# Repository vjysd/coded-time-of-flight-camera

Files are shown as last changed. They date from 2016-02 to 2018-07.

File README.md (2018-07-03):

# Coded Time of Flight Imaging System

## Motivation
Depth accuracy has always been an issue with range imaging technologies. Conventional continuous wave time of flight imaging technologies face multipath, scattering and reflection artifacts. Ultrafast imaging got fascinating ever since Doc Edgerton synchronized his electronic stroboscope with a special high-speed motion-picture-camera so that with each flash, exactly one frame of film was exposed. Visualizing and capturing action at speeds beyond human perception will help us in studying a lot of physical phenomenon like scattering, reflection, and interaction with matter. Here we propose a coded time of flight imaging technique to capture light in motion and to ameliorate depth accuuracy.

## Idea
To address the above mentioned issues, we constructed a coded time of flight camera using the PMD 19k-S3 sensor. This involved design of cyclone IV FPGA, soft core processor programming & optical system development. We carefully chose a broadband code instead of a continuous wave to modulate image sensor and light source. A detailed instrumental manual to build your own coded time of flight camera can be found at the end of this page.

## Approach
We exploited the concept of time resolved imaging to capture light in motion. A phase modulated light source locked with image sensor served this purpose. To address the issue of depth accuracy as our second intent, we constructed a mathematical model of multi-frequency light source de-multiplexing, wherein multiple light sources running at different frequencies were used to improve depth accuracy. A broadband signal, accommodating all the bins from multiple light sources was used to modulate the image sensor. This method proved to be more economical and efficient than current models where multiple cameras are used to serve the same purpose.

## HOW TO
Please use the diy_tof.pdf file to find all the necessary information about rebuilding the system from scratch.

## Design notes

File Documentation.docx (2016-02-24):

ToF Ultra-fast Imaging Camera (Documentation)

Basic Block Diagram:

(This part of the document portrays the important block diagrams which model the system operation.)

Code Database:

(This part of the document depicts various modules/functions/codes which control the overall data and control flow within the scope of the project.)

Verilog modules:

Verilog modules establish an interface between PMD Sensor, ADC and FPGA board and controls their whole operation.

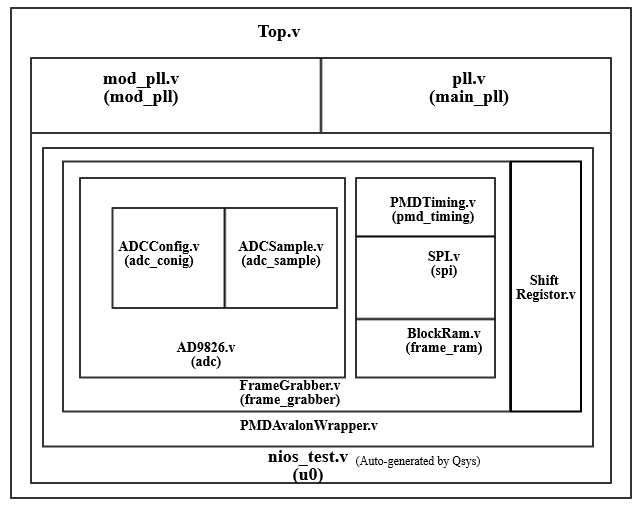
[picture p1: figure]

(Fig2: Verilog Module Flow)

- ADCConfig.v

This FSM configure the FPGA and ADC for a bi-directional data flow. It has three states,

A. STATE_ADDRESS -- Sends the R/W bit, and the three address bits
B. STATE_DELAY -- Pause the operation for few cycles
C. STATE_DATA -- Sends out the 9-bit data word
- ADCSample.v

This FSM controls the Sampling of ADC and the Readout process. It has three states

A. STATE_IDLE -- Waits for the sample_en signal to go high
B. STATE_SAMPLE -- Sample and Hold
C. STATE_READOUT -- Pushes the data into the Bus
- AD9826.v

Instantiates the ADCConfig.v & ADCSample.v and controls the whole ADC bi-directional flow with FPGA.

- PMDTiming.v & SPI.v

These module controls the whole timing operations of the PMD Sensor. They have 16 different states to control the whole flow of IDLE, RESET, INTEGRATION, READOUT, COOLDOWN for PMDTiming, & STATE_DATA, STATE_IDLE, STATE_ADDRESS for SPI . Each of these states meet the timing requirements specified by the PMD Datasheet.

http://web.media.mit.edu/~achoo/pr/19k3_datasheet.pdf

- BlockRam.v

This module controls the reading and writing of ADC readout in and out of FPGA temporary

memory. The data from ADC is moved into a temporary register and then pushed into the Ethernet for data visualization on PC.

- FrameGrabber.v

FrameGrabber instantiates PMD_timing, SPI, BlockRam & AD9826. This FSM has various states to control,

1. Setting frame size.
2. Grabbing the captured frame from the FPGA temporary memory.
- ShiftRegister.v

ShiftRegister module helps in driving the modulating signal to the light source and to the MODSEL terminal of the PMD Sensor.

- PMDAvalonWrapper.v

FrameGrabber is instantiated in this module. It interacts with the C-codes via the address bus and helps to set the Integration time & modulation mode. Since the C-code and the PMDAvalonWrapper are in unison through the address bus, the above specified values can also be set during the compilation of C-codes.

All the above specified modules are fed into the Qsys Library, and when the Qsys is generated, it automatically compiles all the Verilog codes and provides a single interfacing code named nios_test.v.

Qsys can be accessed by going into Tools→ Qsys

- PLL.v

This is a module that is auto generated by using the Megawizard plug-in manager Wizard.

This can be accessed by going into Tools → Megawizard plug-in manager. The interactive GUI guides through the process of configuring the PLL for user requirements.

Here we use PLL.v to generate clock signals of different frequencies, but same phase(i.e. 0). These clocks are used to drive various blocks in the FPGA.

- mod_pll.v

This is a module that is auto generated by using the Megawizard plug-in manager Wizard. Here we use mod_pll, to generate two output clocks of same frequency, but one clock signal configured for dynamic phase reconfiguration. The latter one is fed into the light source, and the former into the MODSEL signal of PMD sensor.

- top.v

This is highest in the hierarchy, and instantiates three modules, i.e. PLL, mod_pll & the nios_test. This acts as a wrapper for the whole Verilog code base.

MATLAB Code & functions:

Matlab codes and functions helps in reading the data from the FPGA ethernet adapter into the Computer and Visualization of the read data.

- pmd_connect.m

This function establishes a tcp/ip connection with the FPGA at a specified port and ip address.

- pmd_read_image.m

This function reads the image data via the tcp port, and shapes it to a specified frame rate and stores it in a variable named rawCorr.

- pmd_phase_step.m

This function writes through the ethernet, specifying the FPGA to increase/decrease the phase of the Light Source.

- pmd_600.m

This matlab code calls the pmd_read_image and thereby captures the frames. The number of frames to be captured can be set in this code. After the frame capture is done, code automatically gets takes the FFT of the frames, and stores it in a variable named rawCorrFFT, and then it plots the angle and the amplitude images using the mview.m function.

- mview.m

This matlab function, inputs the frames captured and provides an interactive GUI to move through all the frames using a mouse scrollbar, and also provides an option to play it at specified frame rates.

C-codes:

C-codes builds a framework to establish a TCP connection between the FPGA board and Computer. These codes program to the soft core processor onboard DE2-115 & help in memory allocation. Alongside that, these codes also helps user to set the Integration time without disturbing the Verilog codebase.

There are mainly two project database to handle the C codes.

- pmd_tcp_bsp

This project helps to generate the Board support packages (BSP) & helps to re allocate the memory changes made in the Verilog code. In order to change update the BSP,

Goto Project Explorer → Right click on pmd_tcp_bsp → Nios 2 → Generate BSP.

- pmd_tcp

This is the C project which controls the whole interface operation. hello_ucosii.c is the main code that is can be used to update the integration time. This code, dumps the Memory write and retrieval code into the soft core processor and establish a bidirectional communication between FPGA and Computer.

FPGA Documentation:

This part of the guide helps in setting up the FPGA board (i.e Altera DE2-115 in this case), to control the timing requirements of PMD 19K-S3 and other peripherals.

There are two ways of setting up the whole environment,

1. Experience the taste of Verilog by setting up everything from Scratch! (We give the codes though).

2. Use the archived project to directly set up the environment.

Setting up required softwares:

1. Quartus ii web edition:

https://www.altera.com/download/software/quartus-ii-we/12.0sp2

2. Nios ii tools:

Download both Version 12.0 and Service pack 2.

https://www.altera.com/download/software/nios-ii/12.0

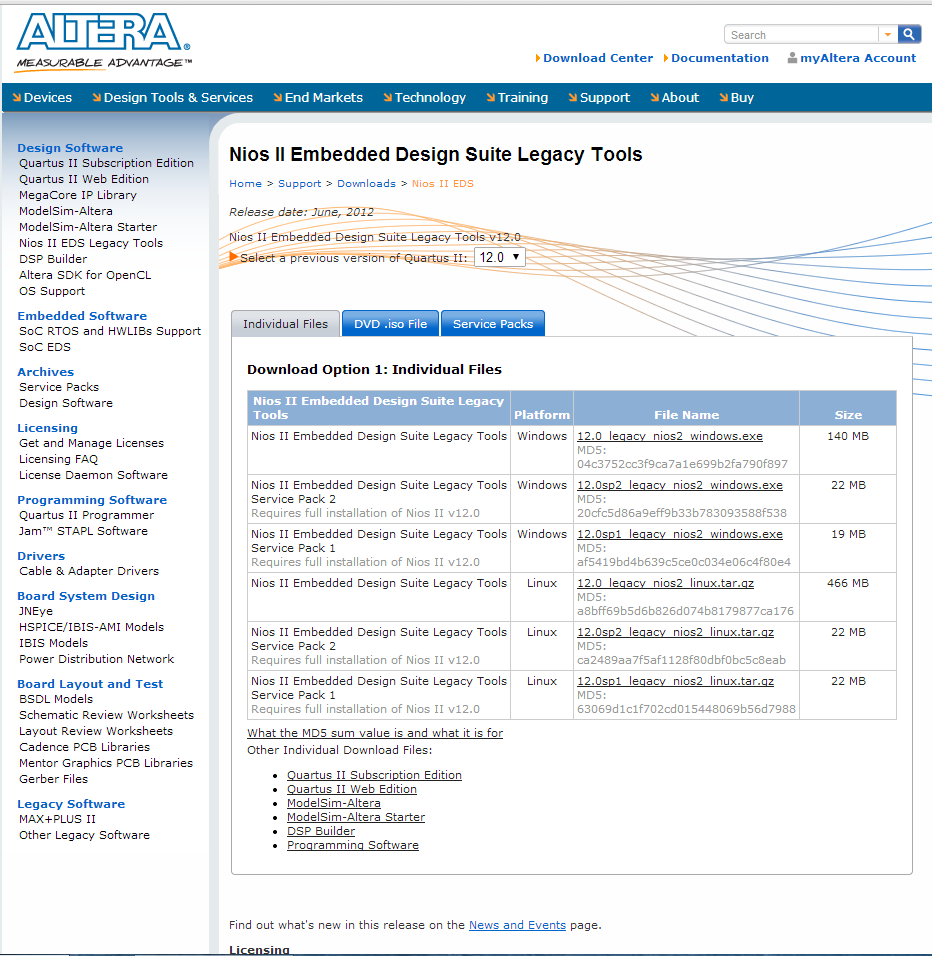
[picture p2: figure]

3. Matlab (Version 2012 or above is preferred).

Steps:

Here are the steps to set up the whole Verilog environment from scratch

1. Once all the softwares are installed and setup, open up Quartus ii → New Project Wizard.

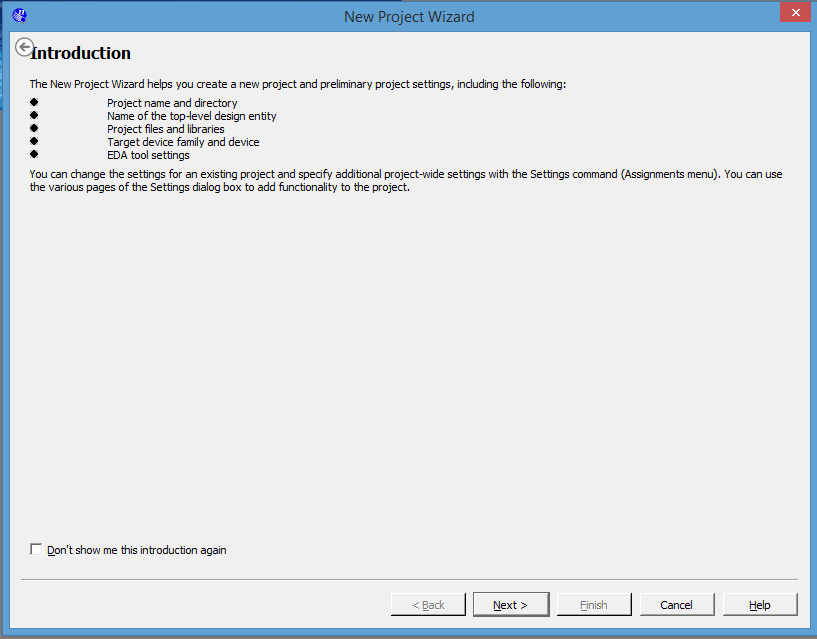
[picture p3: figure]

2. Click on Next, and the window below will pop- up.

- Set the default directory of the project.
- Give a name to the project! (We call this a Nano-Cam!).
- You may define the top level entity as “top”, but we can always modify this later.

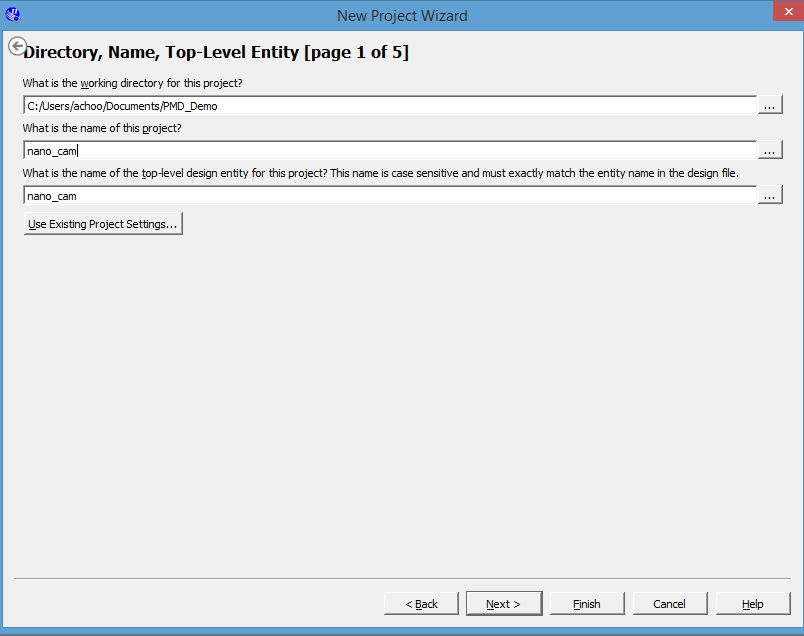
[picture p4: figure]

3. We will be adding all the design files later on, so you can just click on next on the below window.

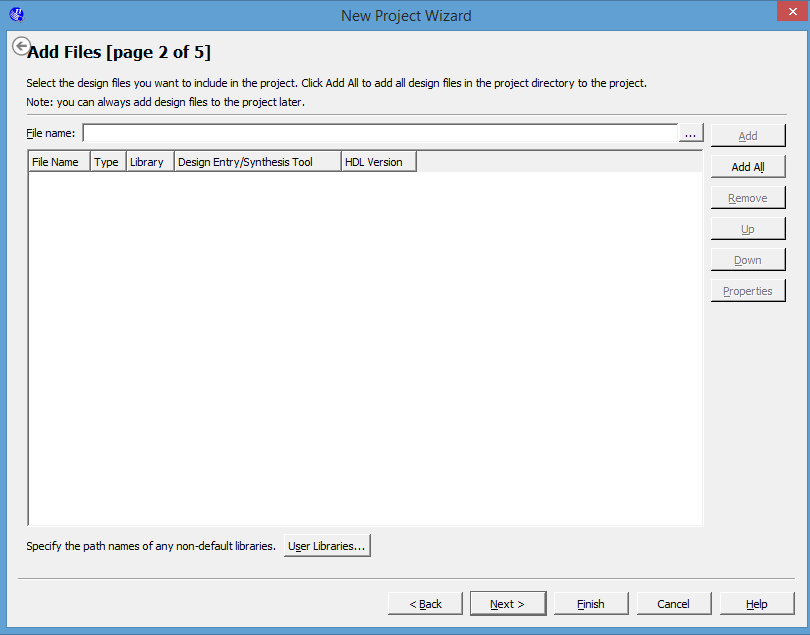
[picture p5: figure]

4. This page defines the FPGA Family and the device we are using.

- Select the Family to be Cyclone 4 E.
- And the device will be EP4CE115F29C7
- Click on next to move forward.

5. This window is to add EDA tools for additional simulation and Verifications, which we can skip and move into next window.

- Finish the project setup wizard.

6. Now we will setup the System map. To do this,

Click on Tools → Qsys, on the top left tab.

7. Once Qsys is up and running, we should see a window below.

8. Now we need to add all the libraries we need,

- On the left, click on Embedded Processors → Nios ii Processor.

Select the core to be Nios ii/s and then click on finish.

- Click on Memories and Memory Controllers → External memory interfaces → SDRAM Interfaces → SDRAM Controller.

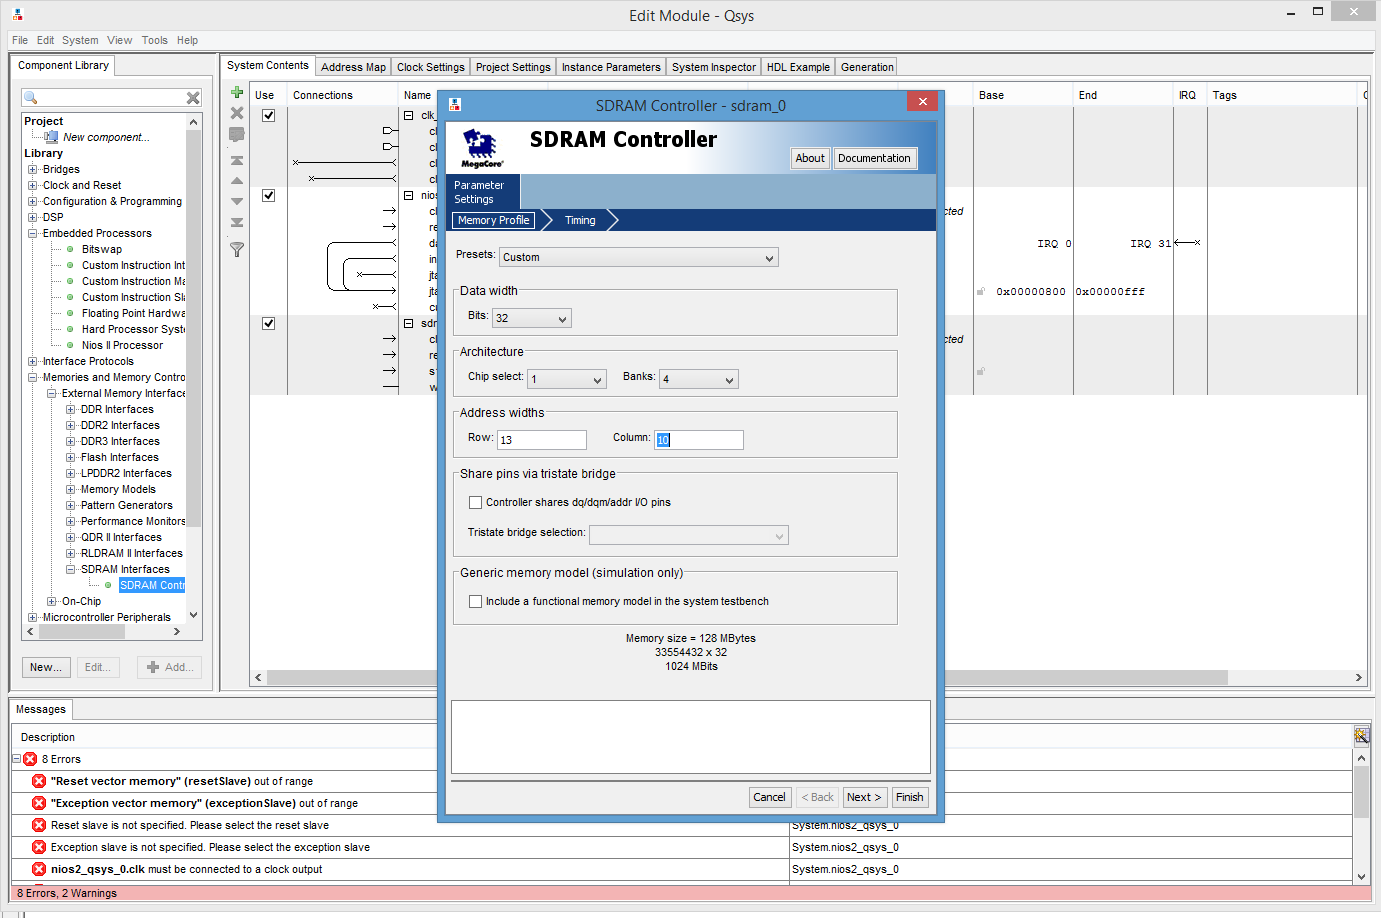
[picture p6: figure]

Select and set the values/parameters as indicated by the figure, and click next.

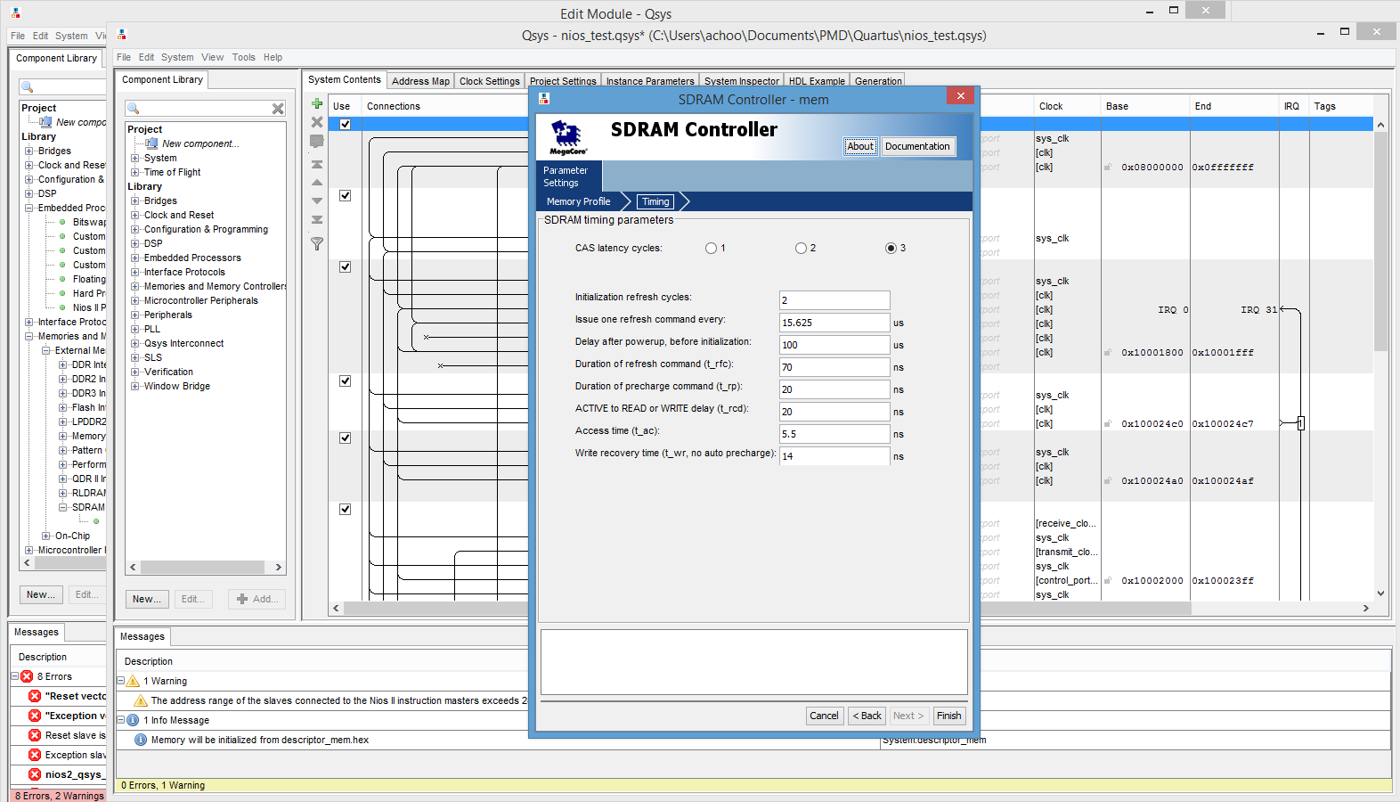
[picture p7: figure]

Now leave the timing parameters as it is and click on Finish.

- Click on Interface Protocols → Serial → JTAG UART to create a new JTAG library from your left pane.

Once the window appears, do not change any settings, click on finish.

- Click on Interface Protocols → Ethernet → Triple Speed Ethernet.

Now follow the below images clicking next, to complete the ethernet library setup. Please enter the values specified in the images to their respective fields.

- Click on Bridges → DMA → Scatter-Gather DMA.

Once the window opens up,

Choose Transfer Mode : Stream to Memory and click on finish.

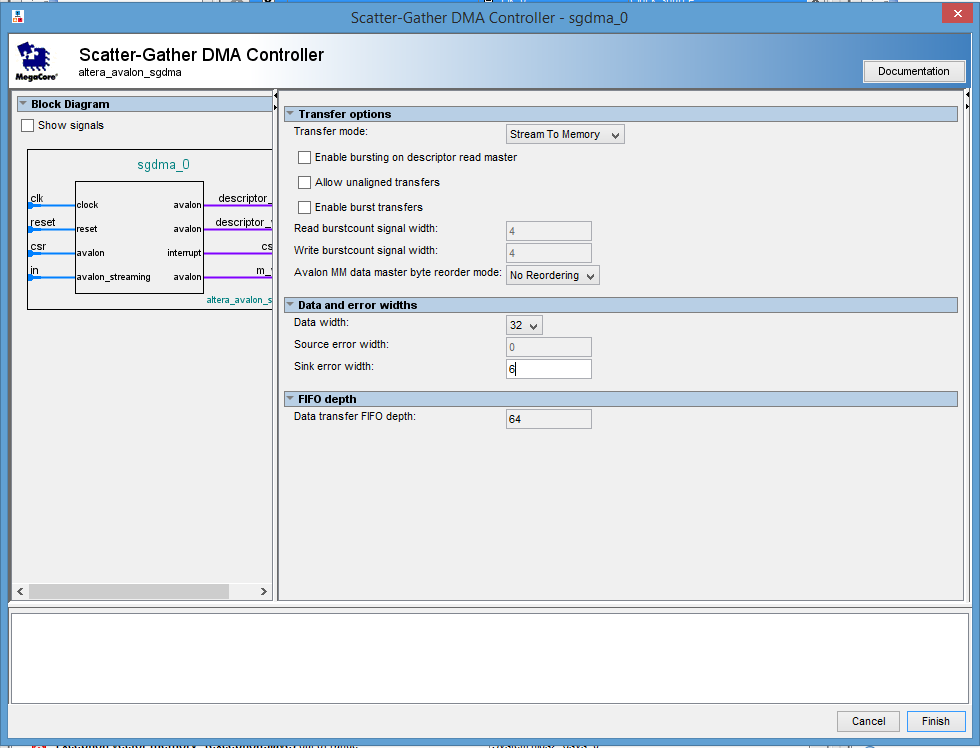
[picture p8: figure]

Repeat the above steps to create another Scatter Gather DMA,

Choose Transfer mode here as: Memory to Stream and click on finish.

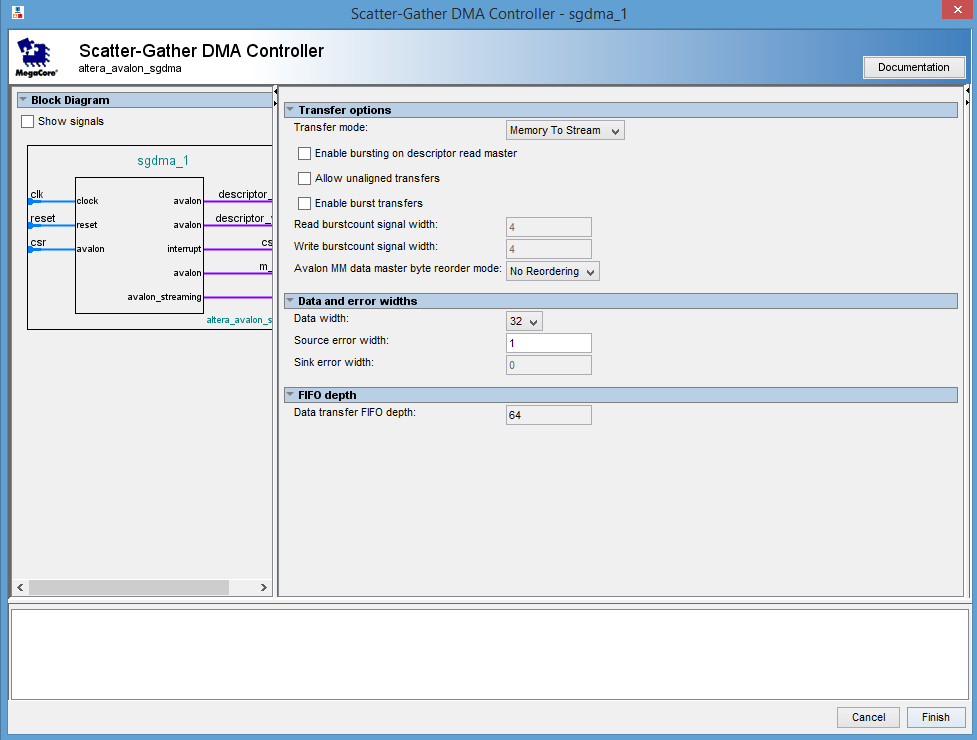
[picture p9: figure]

- Click on Memories and Memory Controllers → On Chip → On Chip Memory (RAM).

Once the window open up, do not edit anything, just click on finish.

- Click on Peripherals → Microcontroller Peripherals → Interval Timer.

Once the window appears click on finish without editing anything.

- Now, we will add our custom library for the Sensor, click on File → New component.

Now enter the following information into the text fields to create the library, and click next.

Click on the “+” button at the left corner to add the verilog files.

After clicking the button, navigate to the folder which is named “Verilog”, within the supplied codebase.

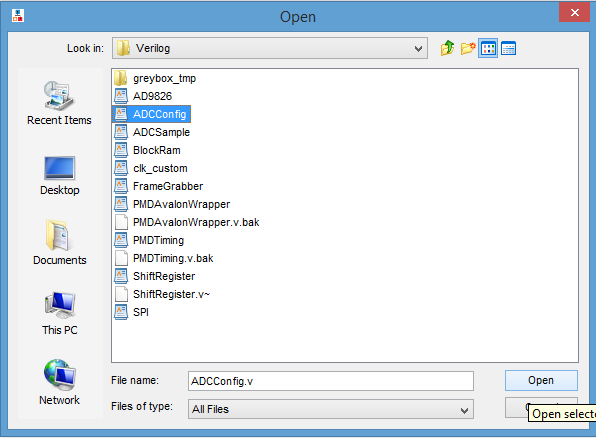
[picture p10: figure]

Select a file and click open. Repeat the above steps till you add all the files in Verilog directory.

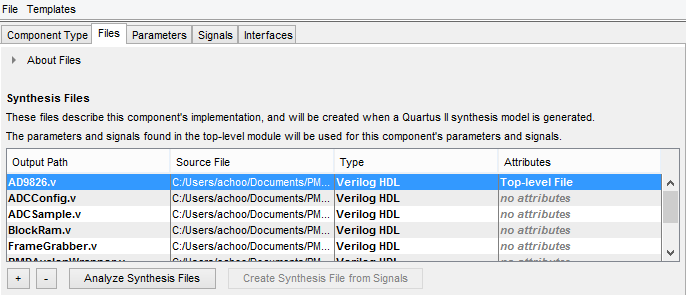
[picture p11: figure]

After all the files are added, the wizard automatically assigns Top-level attribute to the file on the top of the list!! But our top level module is PMDAvalonWrapper. So click on the attribute field on ADC9826, and uncheck top-level attribute.

Navigate to the PMDAvalonWrapper, and set the attribute to be top level file.

Click on ok, and then click on Analyse Synthesis Files. Once the analysis is done, close the console which pops up.

Now click on the Signals tab from the above pane, to edit the signal attributes.

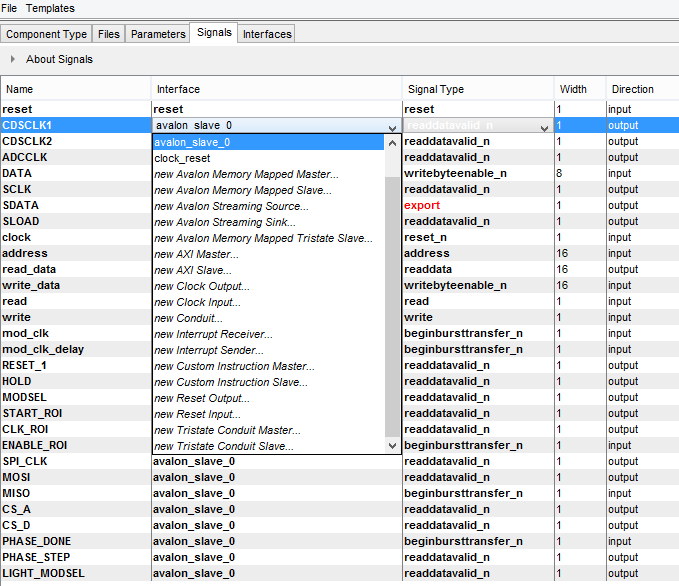
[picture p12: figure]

Here edit all the signals and assign them the properties as shown in the below figure,

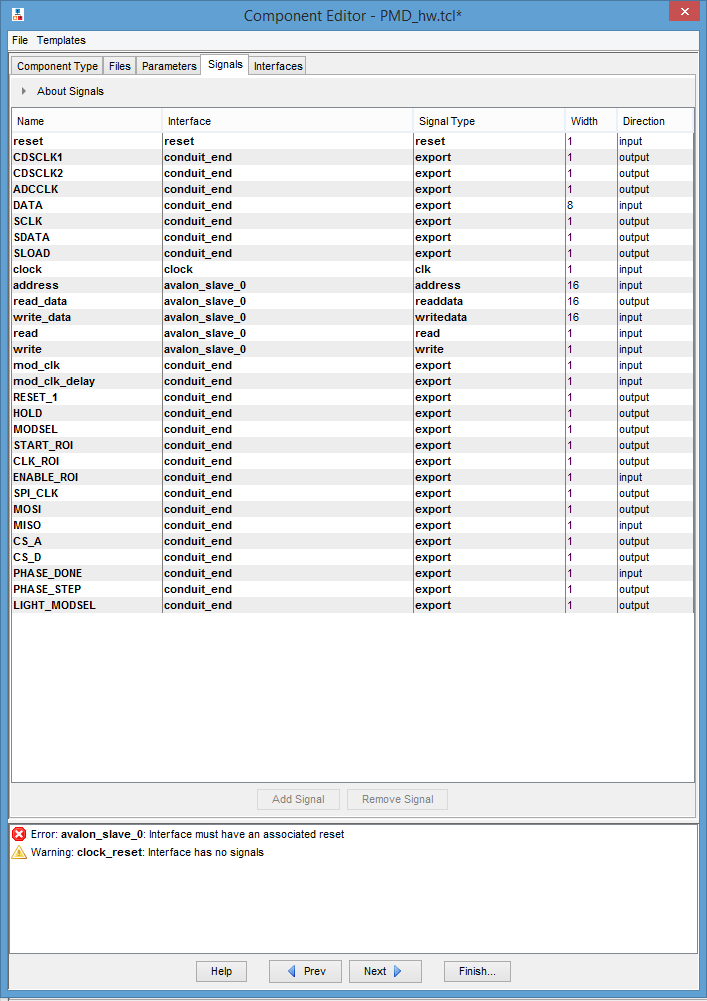
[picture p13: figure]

Once all the signals are edited and set to the specified parameters, click on the next button.

Now go to the interfaces tab, where in select the “clock_reset(Reset input)” interface and click on Remove interfaces with no signal.

Click on finish to add the Custom Library to our system.

9. Once we have added all the libraries into the system, now we need to,

- connect the data and address busses for communication. To do this, we need to move the cursor towards the connections part of the Qsys window.
- Also rename all the components as they are present in the images in order.
- Set the export status of few signals and name them accordingly from the Export section as seen in images.

And click on the dots to form the connectivity as shown in the figures.

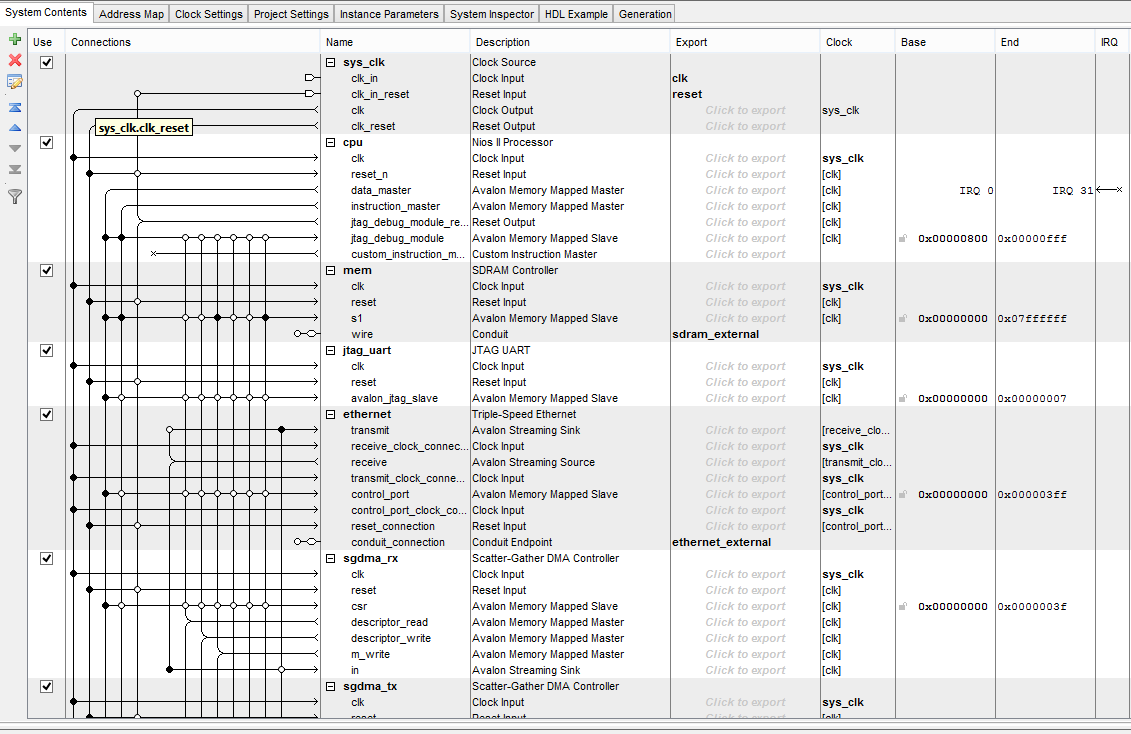
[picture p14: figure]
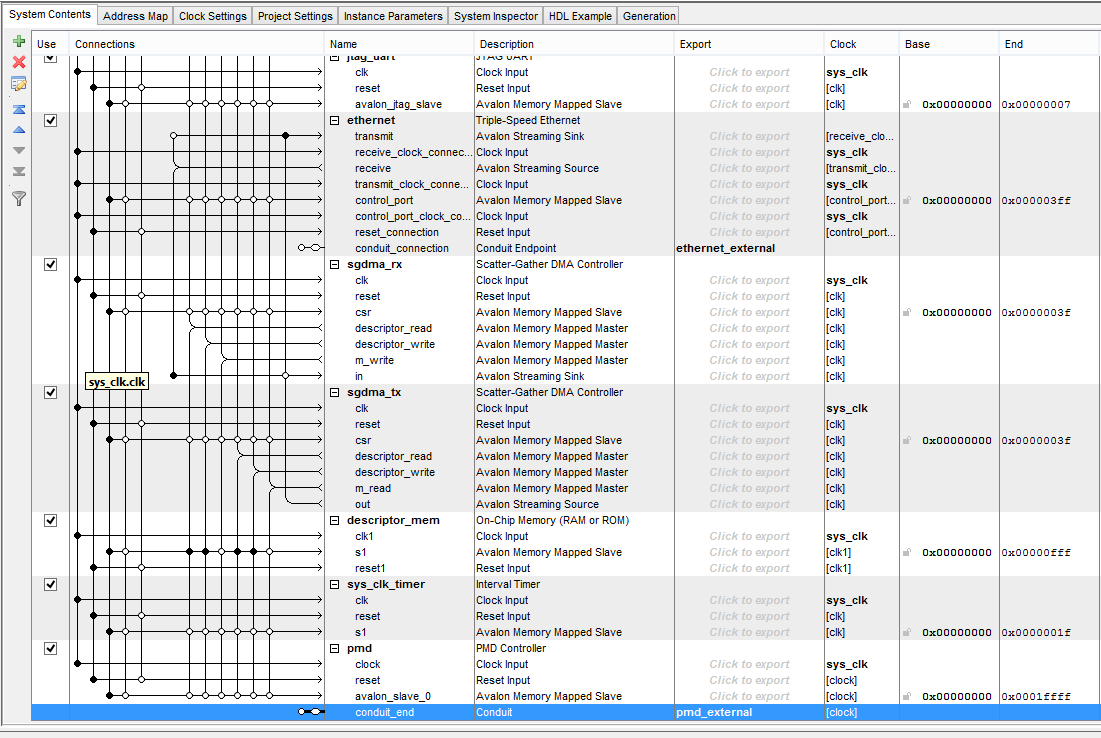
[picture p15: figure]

Once the renaming, connectivity & export assignment is done,

Click on the System → Assign Base Address.

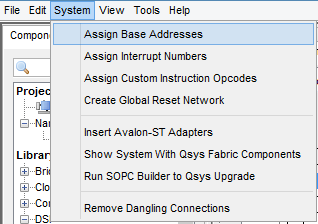
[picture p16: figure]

Now we need to assign the interrupt rank/status to few signals. To do this we will go to the IRQ section in the same Qsys window, and assign values (1, 0, 2, 3) in the tiny boxes there.

Once the interrupt is setup, save the system by going to File → Save or by using (ctrl + S).

Now go into the Generation tab in Qsys, and click on Generate to create the System!

10. Once generate is complete, close the Qsys window. And go back to the Quartus ii project we had created.

11. Click on the Project → Add files into the project.

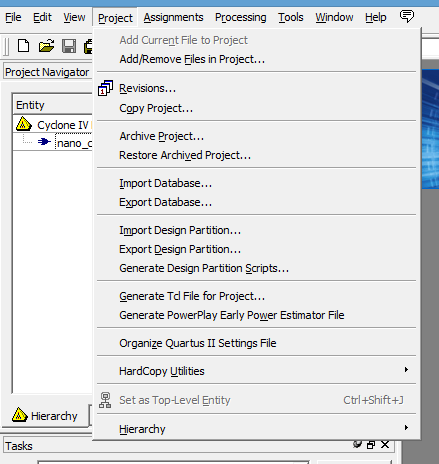
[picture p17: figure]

12. Add the nano_cam.qsys file we just created from the previous steps. To do so, browse to the project location (Done by default).

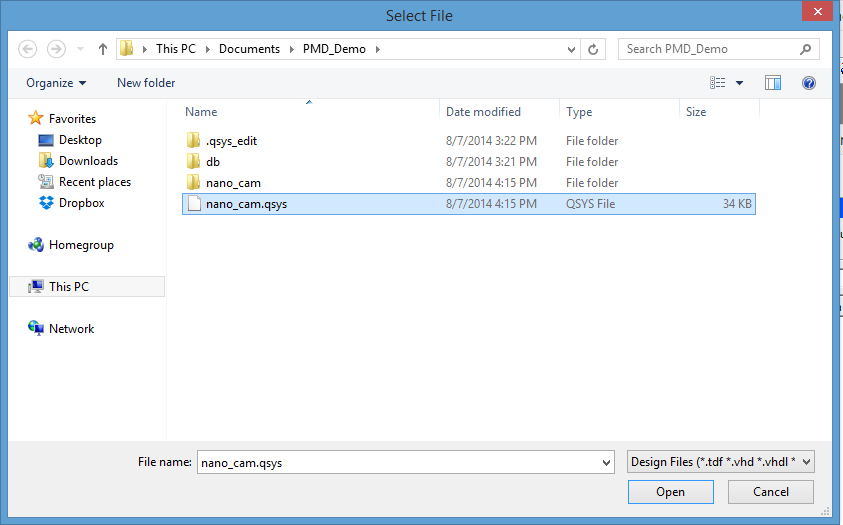
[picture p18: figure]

13. Add top.v file which is provided in the code database by the same steps.

14. We now have to create two PLL (Phase locked loops) to control the light and Sensor modulation. To do this, click on Tools → Megawizard Plug In manager → Create a new custom megafunction variable.

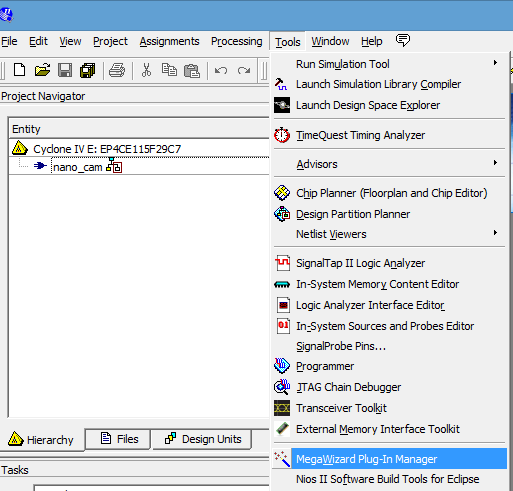
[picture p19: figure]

Search for ALTPLL,

Specify the name of the output file as “pll” and click next.

Follow the below images to navigate through each window and set the parameters likewise. Keep clicking on next to go into next window.

Click on finish to complete the creation of the PLL. If a window pops up asking to automatically update the IP, click OK.

Now similarly we have to create another PLL, named “mod_pll”. This is to give a dynamic phase to one of the signal fed to the light source.

To do this, follow the steps depicted in the pictures below.

(Note that here only two output clocks are used, i.e c0 & c1).

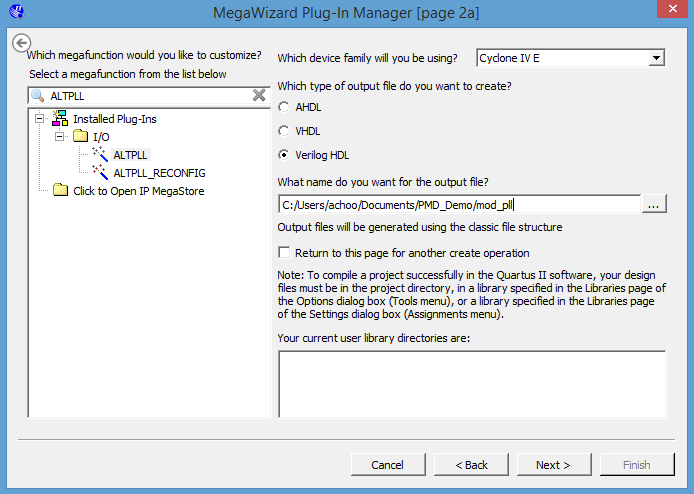
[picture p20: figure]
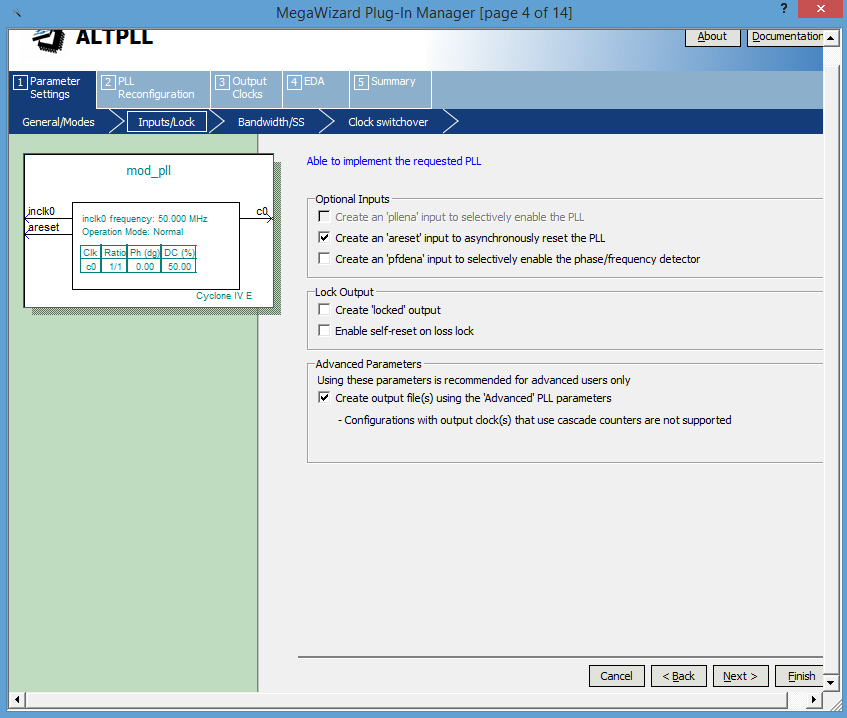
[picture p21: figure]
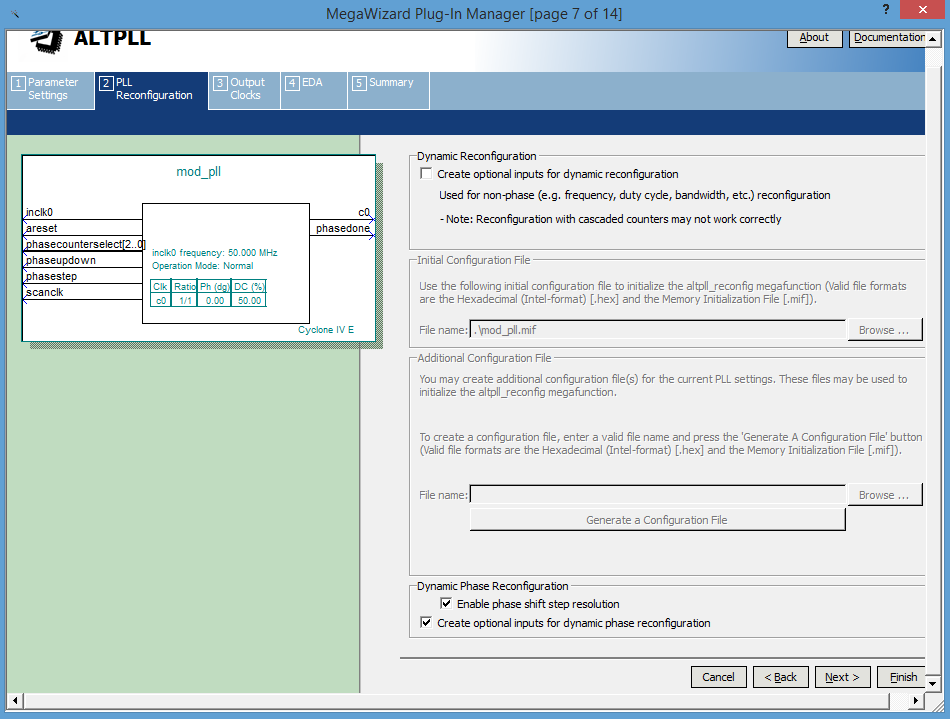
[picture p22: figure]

Here we enable the Dynamic Phase reconfiguration and then the Enable phase step resolution.

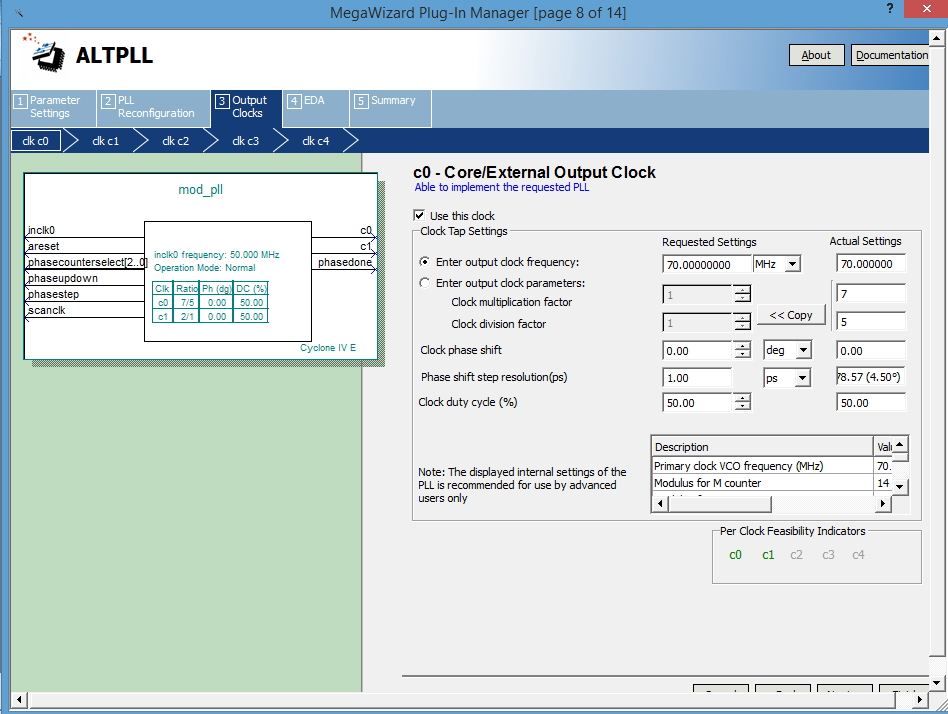
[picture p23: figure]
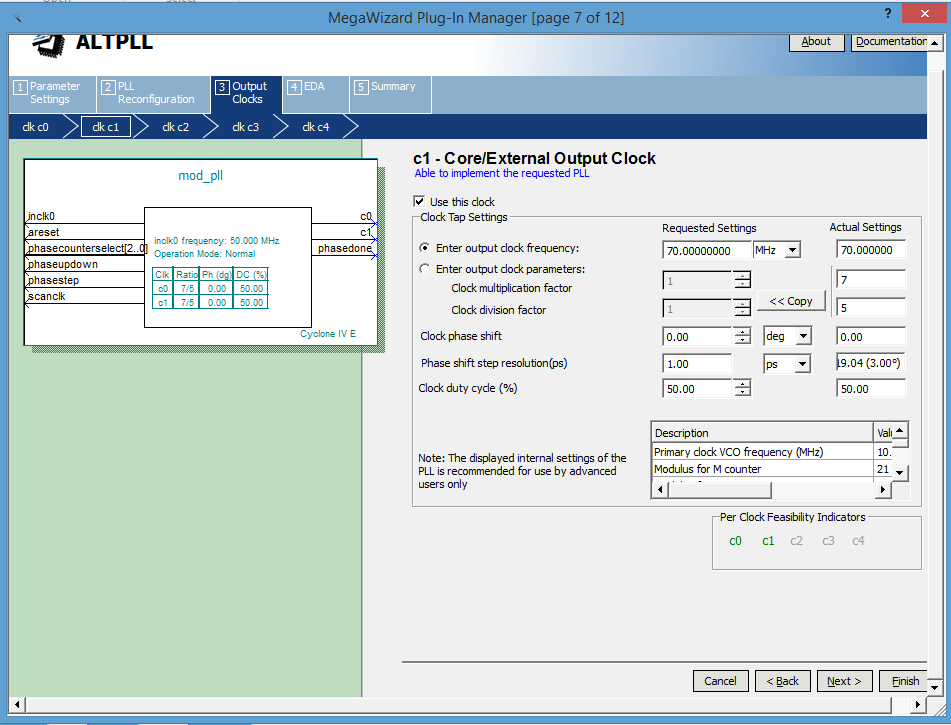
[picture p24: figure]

Click on finish to complete the create the PLL.

15. Now we need to add an IO extension as well for clocking an external pin. To do this, go to Tools → Megawizard Plug In Manager → Create new custom megafunction variation.

Now search for IO, and select “ALTDDIO_OUT”.

Click on next and follow the images below to complete the whole setup.

16. Click on the files tab in the project navigator. And set the top.v as the top level Entity.

17. Finally go to the Assignments → Import Assignments.

Browse to the nano_cam.qsf file which is provided in the code database and click open.

Once this si done, we are ready to compile and program!

18. Click on the Processing → Start Compilation.

This takes around 5-6 minutes to compile and after the we are good to upload and capture some cool depth images!!

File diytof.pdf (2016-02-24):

Vijay Sadashivaiah | Diony Rosa | Achuta Kadambi

### Camera Culture, MIT Media Lab

# Time of Flight – Ultra Fast Imaging Camera

Version
1

# User Reference Manual

# Table of Contents:

### 1. System Architecture

1.1. Block representation
1.2. Brief Overview – Block wise
1.3. Code database & Structure – Language wise

### 2. Printed Circuit Board (Sensor & Light Source)

2.1. Overview on PCB design files
2.2. Circuit Diagrams & Schematics
2.3. Eagle file Database
2.4. Ordering from Sunstone
2.5. Interfacing the PCB’s to FPGA

### 3. Setting up Quartus ii Verilog programming Environment

3.1. Quartus Download & Setup
3.2. Archived project – Importing and Setup
3.3. Compilation and Verification

### 4. Setting up Nios ii hardware interface tool

4.1. Archived project – Importing and Setup
4.2. Compilation and Verification

### 5. Setting up MATLAB programming Environment

5.1. Code Database – Scripts & Functions
5.2. Setting the parameters
5.3. Workflow & Representation

### 6. Calibration and Capture 7. Appendix 1-2

# System Architecture

This part of the document explains the whole system architecture and signal flow within the Camera.

1.1. Block Diagram Representation


(Fig1: Block diagram of various sub elements)

Part
1

1.2. Brief Overview – Block Wise

As seen in the Block diagram, the whole system comprises of 3 main blocks. In this section we will briefly describe each one of them and provide additional resources.

1.2.1. Altera DE2-115 Development kit:

The Altera® DE2-115 Development and Education board was designed by professors, for professors. It is an ideal vehicle for learning about digital logic, computer organization, and FPGAs. Featuring an Altera Cyclone® IV 4CE115 FPGA, the DE2-115 board is designed for university and college laboratory use. It is suitable for a wide range of exercises in courses on digital logic and computer organization, from simple tasks that illustrate fundamental concepts to advanced designs.

Official link to website and purchase information for Academic research: http://www.altera.com/education/univ/materials/boards/de2-115/unv-de2-115-board.html (http://www.altera.com/education/univ/materials/boards/de2-115/unv-de2-115-board.html)

1.2.2. PMD 19K – S3:
The PMD PhotonICs® 19k-S3 is the first commercially available Time-of-Flight 3D chip. The optical sensor enables the real-time capture of distance and gray scale information. Due to the outstanding sensitivity and improved performance of the new PMD Photo-nICs® 19k-S3, high accuracy with extremely low power consumption is achievable. Read-out clocks of 15MPixel/s are possible. Thanks to the integrated SBI (Suppression of Background Illumination) technology, a well-known PMD feature, this innovative product can be deployed in indoor and outdoor environments.

Official link to website:
http://www.pmdtec.com/products_services/pmd_photonics.php


1.2.3. Illumination System:

Illumination forms a very important part of time of flight imaging, and we are using a Laser source to drive our Camera system. We have used a single, LPC-826 Laser diode from Mitsubishi. These are High speed lasers which serves our purpose of bright illumination.

It is very important to choose an efficient driver to handle high current requirements of Laser diode. We used the iC- HG HG1D evaluation board from iC – Haus to efficiently drive the Laser.

1.2.4. Other peripherals and blocks:
- Other than these three blocks, AD9826K is an Analog to Digital converter used to achieve sampling and readout from the Sensor into the FPGA. Timings and operation is again controlled by the DE-115 board.
- Onboard PLL (DE2-115), is used for achieving phase and frequency modulations, thereby providing a phase lock system for the operation of Camera.

- A computer system forms a medium to configure all the peripherals and also to visualize the data captured from the camera. We use mainly three software packages for working with our camera.
a. Quartus ii FPGA programming interface
b. Nios ii Hardware tool package
c. MATLAB
1.3. Code Database:

This part of the document depicts various modules/functions/codes which control the overall data and control flow within the scope of the project.

1.3.1. Verilog modules:

Verilog modules establish an interface between PMD Sensor, ADC and FPGA board and controls their whole operation.


(Fig2: Verilog Module Flow)

Verilog Files/Archive project can be downloaded: http://tinyurl.com/l7gzmnv

1.3.2. Matlab scripts/Functions:

Matlab codes and functions helps in reading the data from the FPGA ethernet adapter into the Computer and Visualization of the read data.

Matlab Files/Scripts can be downloaded at: http://tinyurl.com/oluath7

1.3.3. C-codes Nios interface:

C-codes builds a framework to establish a TCP connection between the FPGA board and Computer. These codes program to the soft core processor onboard DE2-115 & help in memory allocation. Alongside that, these codes also helps user to set the Integration time without disturbing the Verilog codebase.

C-codes can be downloaded at: http://tinyurl.com/l8l4p3o

Here is a link to brief explanation of each module/ function:

http://tinyurl.com/nt3omx5

http://tinyurl.com/jlspyvo (http://tinyurl.com/l7gzmnv)

http://tinyurl.com/jguunla (http://tinyurl.com/nt3omx5)

All the project codes are available here: Download as zip and unzip the files,

https://github.com/vjs347/coded-time-of-flight-camera

# Printed Circuit Board

(Sensor & Light Source)

This part of the Document illustrates the PCB layouts & Circuit diagrams of the light source and Sensor used for the Camera. This forms the first step towards building your own time of flight imaging device.

2.1. Overview:

Circuit Diagrams/Schematics & PCB Design forms the first step towards building any electronic gadget. In our Camera, we have two important PCB designs,

2.1.1. Sensor board Design:

The PMD 19K-S3 sensor from PMD Photonics, is a 40 pin IC. The terminals are interfaced with the ADC and the FPGA to control the timing and readout. It requires precision design capabilities and ideas in designing the whole sensor board. We have used AD9826K ADC for the readout.

2.1.2. Light Source design:
We have used a single, LPC-826 Laser diode from Mitsubishi. These are High speed lasers which serves our purpose of bright illumination. iC- Haus HG1D evaluation board is used to drive these High power Lasers.

Part
2

2.2. Circuit Diagrams and Schematics:

In this section we briefly describe the Circuits/ Schematics used in our design. Appropriate images are added for reference.

2.2.1. Sensor Schematic:
a. Voltage Regulator:


This forms the Voltage regulator circuit to drive/power the PMD Sensor board from the FPGA.

b. 40 Pin connector:


This forms the 40 pin Connector which is the main interface bus between DE2-115 and Sensor board.

c. ADC Circuit:


ADC here works in Sample and hold mode and helps in sampling the analog readout from the sensor and pushes the data into the FPGA through the 40 pin connector.

In the figure the terminals VIDEO01, VIDEO02, VIDEO03 are the input signals
into the ADC and the terminals named ADC00…….ADC07 frames the output of
the ADC data.

d. PMD 19K-S3 Sensor:

All the Signals to control the timing of PMD are coming from the FPGA board.

The whole Schematic image could be found at: http://tinyurl.com/m5ko9k6
https://github.com/vjs347/coded-time-of-flight-camera/tree/master/_PCB/Sensor

2.2.2. Light Source Schematic:

The Schematic and the mapping for HG1D evaluation board can be found here.

http://www.ichaus.de/upload/pdf/HG_datasheet_B2en.pdf

2.3. Eagle File Database:

All the schematics and board design files (both schematic and board) can be downloaded at:

http://tinyurl.com/nj8xxj5

2.4. Ordering from Sunstone:

Sunstone Circuits is one of the most experienced PCB manufacturers in the USA. All the orders can be placed online by uploading the Schematics and the board files.

Official link: www.sunstone.com

2.5. Interfacing the PCB and FPGA:

This section illustrates the steps to be followed to wire up the Sensor board & Light source to the FPGA.

Steps to be followed:

1. Once the PCB’s are fabricated, and soldered with all the components as
in the schematic, the Sensor should look something like this.

https://github.com/vjs347/coded-time-of-flight-camera/tree/master/_PCB/Light_Source/New (http://tinyurl.com/nj8xxj5)


2. Now attach the 40 pin connector to the port in the image and connect the other end to the 40 pin connector on FPGA Development kit. After the connection is done, the system should look like,


3. Once this is done, now we need to hook up the light source, to do this, connect the terminals circled in red on Light source board, to the pins on DE2-115 marked red in the adjacent diagram.


Power up the Evaluation board with plugging VDD and VLDA to ~4V. This completes the whole process of integrating light source and Sensor board to the FPGA.

# Setting up Quartus Environment

(Verilog HDL programming)

This section deals with setting up the whole Verilog environment on Quartus ii software package. Quartus ii is a software platform to develop Verilog projects and provides all the toolbox for its integration with Altera FPGA kits.

Here we use Altera DE2-115, Cyclone 4 E FPGA which performs these important tasks,
- Control all the timing requirements of PMD 19K-S3 and ADC.
- Readout data from ADC and push it into the Computer.
- PLL to synthesize the required modulated clocks.
3.1. Quartus Download and Setup / Compilation & Verification

This section helps in downloading the required Quartus version and installation. We prefer using Quartus ii 12.0 edition, since it is stable. Newer versions can also be used.

Part
3

3.1.1. Quartus ii is a licensed software, but we can use a web edition for our requirements. To download Quartus ii web edition, go to link:

https://www.altera.com/download/software/quartus-ii-we/12.0sp2


On the webpage download the required file depending on the platform. In this documentation we follow the installation on Windows PC. Although Linux will have a similar setup procedure.

3.1.2. Ways to setup Quartus environment:

There are two ways of setting up the whole environment,

1. Experience the taste of Verilog by setting up everything from Scratch! (We give the codes though).
To setup everything from scratch, follow this link: http://tinyurl.com/nuols39
2. Using the archived project to directly set up the environment.

In this document we depict the procedure to setup the Verilog environment from the Archived project.

3.2. Archived Project – Import & Setup:

To ease the process of setting up the Verilog environment on Quartus ii, we have created an archive file of the project. This section will illustrate how to download → Import → Setup the project database.

Steps to be followed:

### 1. To download the archive project, navigate to the below link

http://tinyurl.com/l7gzmnv

### 2. Now download all the contents that are present in the “Quartus”

and “Verilog_files” directories and place them on any of your computer directory.

### 3. After this is done, now open the Quartus ii Software from your

computer.

### 4. Now close the small pop-up that appears asking you to create a

new project/open a project.
5. Now navigate to project tab on the top left,

Project → Restore Archived project

Use the Setting up Verilog from (http://tinyurl.com/nuols39) Scratch.docx

https://github.com/vjs347/coded-time-of-flight-camera/tree/master/_Codes/_Verilog (http://tinyurl.com/l7gzmnv)


### 6. Now navigate to the path where you have downloaded the archive

files.


### 7. Now specify the required output directory and name on this

window.


### 8. After the project restoration is complete, now go to the path where

you restored the project and delete the folders named “db”,
“incremental_db” & megafunctions. (Note that you need to close Quartus window to delete these folders).

### 9. In the same directory, open the file named “PMD_hw.tcl” and

change the directory of files specified, to the path where you have
saved the Folder “Verilog_files” from the google drive download link. (Note that you should use ‘/’ symbol and not ‘\’).

### 10. Now close that file and open the Quartus project again, now go to

Tools → Qsys

11. Select the nios_test.qsys file from the window and click open.


### 12. Close the completion dialog and navigate into the Generate tab in

Qsys.


13.Once generate is complete, save the System with (ctrl+S), and close Qsys.
14. Now compile the Verilog project by navigating into,
Processing → Start Compilation.

Wait for the whole project to get complied and synthesized. (This usually takes 5~6 minutes).
15.Once compilation is complete you can run the programmer by going to Tools → Programmer.
16.After opening the programmer, you can follow the instructions on this page to setup the hardware. http://www.altera.com/download/drivers/dri-quartus.html

There might be some issues with the JTAG Server installation. To overcome this follow instruction on,
http://www.altera.com/support/kdb/solutions/rd02212013_169.html
(Make sure you start the JTAG Server by using command jtagserver --start)
→ Finally even after all this, if the Hardware is not detected, Go to Control Panel→ Device Manager→ And make sure the USB-Blaster driver is installed. If not, install the drivers by navigating to the drivers folder in C:/Altera/12.0/quartus/drivers.
17.After the hardware is setup and detected, click on Start to program the FPGA!

These are the steps involved in setting up the whole Verilog environment. Now we can move on to programming the soft-core processor on Nios ii.

# Setting up Nios ii Environment

(C-codes to program soft – core processor)

This section of the document depicts the procedure to setup the Nios ii platform to program the Soft – core Processor. Nios ii EDS package usually comes with the Quartus package itself.

Here the main purpose of Nios is to work as a medium to,
- Temporarily save the readout data from Sensor.
- Push this data via Ethernet from FPGA to the Computer.
- Also creates an active bus to pass few parameters from matlab programming console.
4.1. Archived Project – Import & Setup/Compilation

This section deals with the importing of Archived C code from the code database and setting up the Nios ii environment.

Steps to be followed:

1. Archived project is available on the link:
http://tinyurl.com/l8l4p3o
2. Download the zip file named “Cfiles.zip”.
3. Now open the Nios ii from the Computer and specify your workspace to some path.

Part
4

https://github.com/vjs347/coded-time-of-flight-camera/tree/master/_Codes/_C_Codes (http://tinyurl.com/l8l4p3o)


4. Navigate to File → import → General → Add existing projects to Workspace.
5. Now choose to import from Archive project and navigate to the path where Cfiles.zip was downloaded and click open.

6. Once the projects are imported, right click on pmd_tcp_bsp → Nios ii → Generate BSP.


7. Right click on the pmd_tcp_bsp → Build Project. Once the build is complete now, repeat this step to build even the pmd_tcp project.
8. After building pmd_tcp project, we need to run the pmd_tcp project, to do this, click on Run → Run. If a pop up asks for Run as, choose Nios ii Hardware.

→ If there is an error popping out goto Run→ Run Configurations→ Nios 2→Target Devices Tab And check ignore mismatch system id and system timestamp.

After these steps, the Nios ii will compile and dump the required code into the soft – core processor and establishes a connecting with FPGA. Now we can call the matlab functions / Scripts to capture some data!

# Setting up MATLAB Programming Environment

(Matlab Scripts and Functions)

This section of the document depicts the last software package to be setup for the data capture. MATLAB is a programming environment created by MathWorks. We have written few MATLAB functions and Scripts to set parameters and capture data from the Camera.

MATLAB is a licensed software, and can be directly downloaded from the official website,
http://www.mathworks.com/products/matlab/
5.1. Code Database: Download and Setup:

All the matlab codes required for the Camera are available at the web link:

http://tinyurl.com/oluath7. Download all the files and save them in a directory.

Part
5

https://github.com/vjs347/coded-time-of-flight-camera/tree/master/_Codes/_Matlab

5.2. Setting the Parameters:

This is an important section which determines where to set the parameters like Integration time, Custom code, Number of steps etc.

Here we depict this using code snippets and function calls,

5.2.1. Setting the Integration time:


To set integration time, we can call the pmd_set_integration_time function from the command prompt. Above snippet indicates its operation.

5.2.2. Setting the Phase step size and number of averages:


To set the Phase step
size and the number
of averages of every
frame we can use this
function, where in we
can specify these
values in the function
call.

5.3. Workflow and Representation:

This section will indicate how the actual capture of data happens across the software packages. We will start with calling the matlab function pmd_600.m.


(Figure: The data and control flow within matlab)

With all the above procedure and setup, the Ultra-fast Camera is ready for a capture!

# Appendix 1:

# Setting the Modulating frequency:

To set the modulation frequency of the signal driving light source and PMD in phase lock, we have to edit the Mega wizard plugin manager.

To do this,
1. Open the Quartus project → Tools → Mega Wizard Plugin Manager


2. Edit existing custom megafunction variation.
3. Choose modpll.v from the list of design,

4. Now navigate to the output clocks tab and substitute the value of frequency required. (Note that you need to give the same value to both c0 and c1 which drives MODSEL and Light modulation code respectively.)


(The value entered is twice the frequency required. i.e. if you need 60 MHz of modulation, you enter 120 MHz here).

5. Click on finish and confirm the screen which says few files will be modified.


Once the modification is done, you need to recompile the Verilog design and upload it onto FPGA.

# Appendix 2:

# Setting the custom Modulation code:

To set the required modulation code, we will have to convert the binary code of 1’s and 0’s into hex notation and divide it into two equal halves. Say the custom code
required is,
01011101100011111001101001000010. To easily simplify, go to www.wolfromalpha.com
And ask for the hex version of this code by writing in the box, “01011101100011111001101001000010 to hex”. The output will be,

→
Dividing this into halves, we get 5d8f & 9a42.

To change the code into this custom value, navigate to the C code, hello_ucosii.c


In the above part of snippet, place the two codes accordingly and recompile the c code.

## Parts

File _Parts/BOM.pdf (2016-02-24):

No. | Qty | Ref | Manufacturer | Mfg. Part # | Dest. Part #(Digi-Key) | Description | Pkg | Type | $
1. | 12 | C1, C2, C3, C4, C5, C6, C7, C10, C11, C12, C13, C14, C18, C19 | Kemet | C0805C104K5RACTU | 399-1170-1-ND | CAP CER 0.1UF 50V 10% X7R 0805 | 0805 | SMT | 0.5
2. | 2 | C8, C16 | Kemet | C0805C105K4RACTU | 399-1284-1-ND | CAP CER 1UF 16V 10% X7R 0805 | 0805 | SMT | 0.22
3. | 3 | C9, C15, C20 | Kemet | C0805C106K8PACTU | 399-4925-1-ND | CAP CER 10UF 10V 10% X5R 0805 | 0805 | SMT | 0.54
4. | 1 | C17 | Panasonic Electronic Components | EEE-1EA101P | PCE3896CT-ND | CAP ALUM 100UF 25V 20% SMD | Radial Can | SMT | 0.64
5. | 1 | JP1 | Sullins Connector Solutions | SBH11-NBPC-D20-SM-BK | S9192-ND | CONN HEADER 2.54MM 40POS GOLD SMD | Header | SMT | 1.71
6. | 1 | R8 | Stackpole Electronics Inc | RMCF0805FT464R | RMCF0805FT464RCT-ND | RES 464 OHM 1/8W 1% 0805 | 0805 | SMT | 0.09
7. | 1 | R9 | Stackpole Electronics Inc | RMCF0805FT240R | RMCF0805FT240RCT-ND | RES 240 OHM 1/8W 1% 0805 | 0805 | SMT | 0.09
8. | 1 | R2 | Stackpole Electronics Inc | RMCF0805FT3K74 | RMCF0805FT3K74CT-ND | RES 3.74K OHM 1/8W 1% 0805 | 0805 | SMT | 0.09
9. | 1 | R3 | Stackpole Electronics Inc | RMCF0805FT1K30 | RMCF0805FT1K30CT-ND | RES 1.3K OHM 1/8W 1% 0805 | 0805 | SMT | 0.09
10. | 1 | R6 | Stackpole Electronics Inc | RMCF0805FT2K80 | RMCF0805FT2K80CT-ND | RES 2.8K OHM 1/8W 1% 0805 | 0805 | SMT | 0.09

11. | 1 | R7 | Stackpole Electronics Inc | RMCF0805FT2K20 | RMCF0805FT2K20CT-ND | RES 2.2K OHM 1/8W 1% 0805 | 0805 | SMT | 0.09
12. | 1 | R4 | Stackpole Electronics Inc | RMCF0805FT1K20 | RMCF0805FT1K20CT-ND | RES 1.2K OHM 1/8W 1% 0805 | 0805 | SMT | 0.09
13. | 1 | R5 | Stackpole Electronics Inc | RMCF0805FT3K83 | RMCF0805FT3K83CT-ND | RES 3.83K OHM 1/8W 1% 0805 | 0805 | SMT | 0.09
14. | 1 | U1 | PMD Tec | 19K-S3 | (Not available on Digikey, Contact sales@pmdtec.com) | PMD Tof Sensor | TLCC40 | QFN | 300
15. | 1 | U2 | Analog Devices | AD9826KRSZ | AD9826KRSZ-ND | IC IMAGE SGNL PROC 16BIT 28-SSOP | SSOP28 | SMT | 10.03
16. | 1 | U3 | Texas Instruments | TLV1117CDCYR | 296-17598-1-ND | IC REG LDO ADJ 0.8A SOT223 | SOT223 | SMT | 0.57
17. | 1 | R1 | Bourns Inc | 3386X-1-103TLF | 3386X-103TLF-ND | TRIMMER 10K OHM 0.5W PC PIN | Square | Thru Hole | 2.11
18. | 1 | U4 | Ic-Haus | HG1D | (Not available on Digikey, Order on www.ichaus.de) | 3A Laser Switch Eval Board | ---------- | ------ | 75
19. | 6 | L1 | Mitsubishi | LPC-826 | (Not available on Digikey, Order on laser66.com) | Pulsed Laser Diode | TO18 | Thru Hole | 84
20. | 1 | L2 | Thor Labs | CMR | (Not available on Digikey, Order on thorlabs.com) | C mount Lens Holder | C Mount | ------ | 29
21. | 1 | L3 | Thor Labs | MVL16L | (Not available on Digikey, Order on thorlabs.com) | C mount Lens-16mm | C mount | ------ | 240
22. | 1 | L4 | Altera | DE2-115 | (Not available on Digikey, Order on altera.com) | FPGA Dev kit | ---------- | | 300

Total Cost: 1045$

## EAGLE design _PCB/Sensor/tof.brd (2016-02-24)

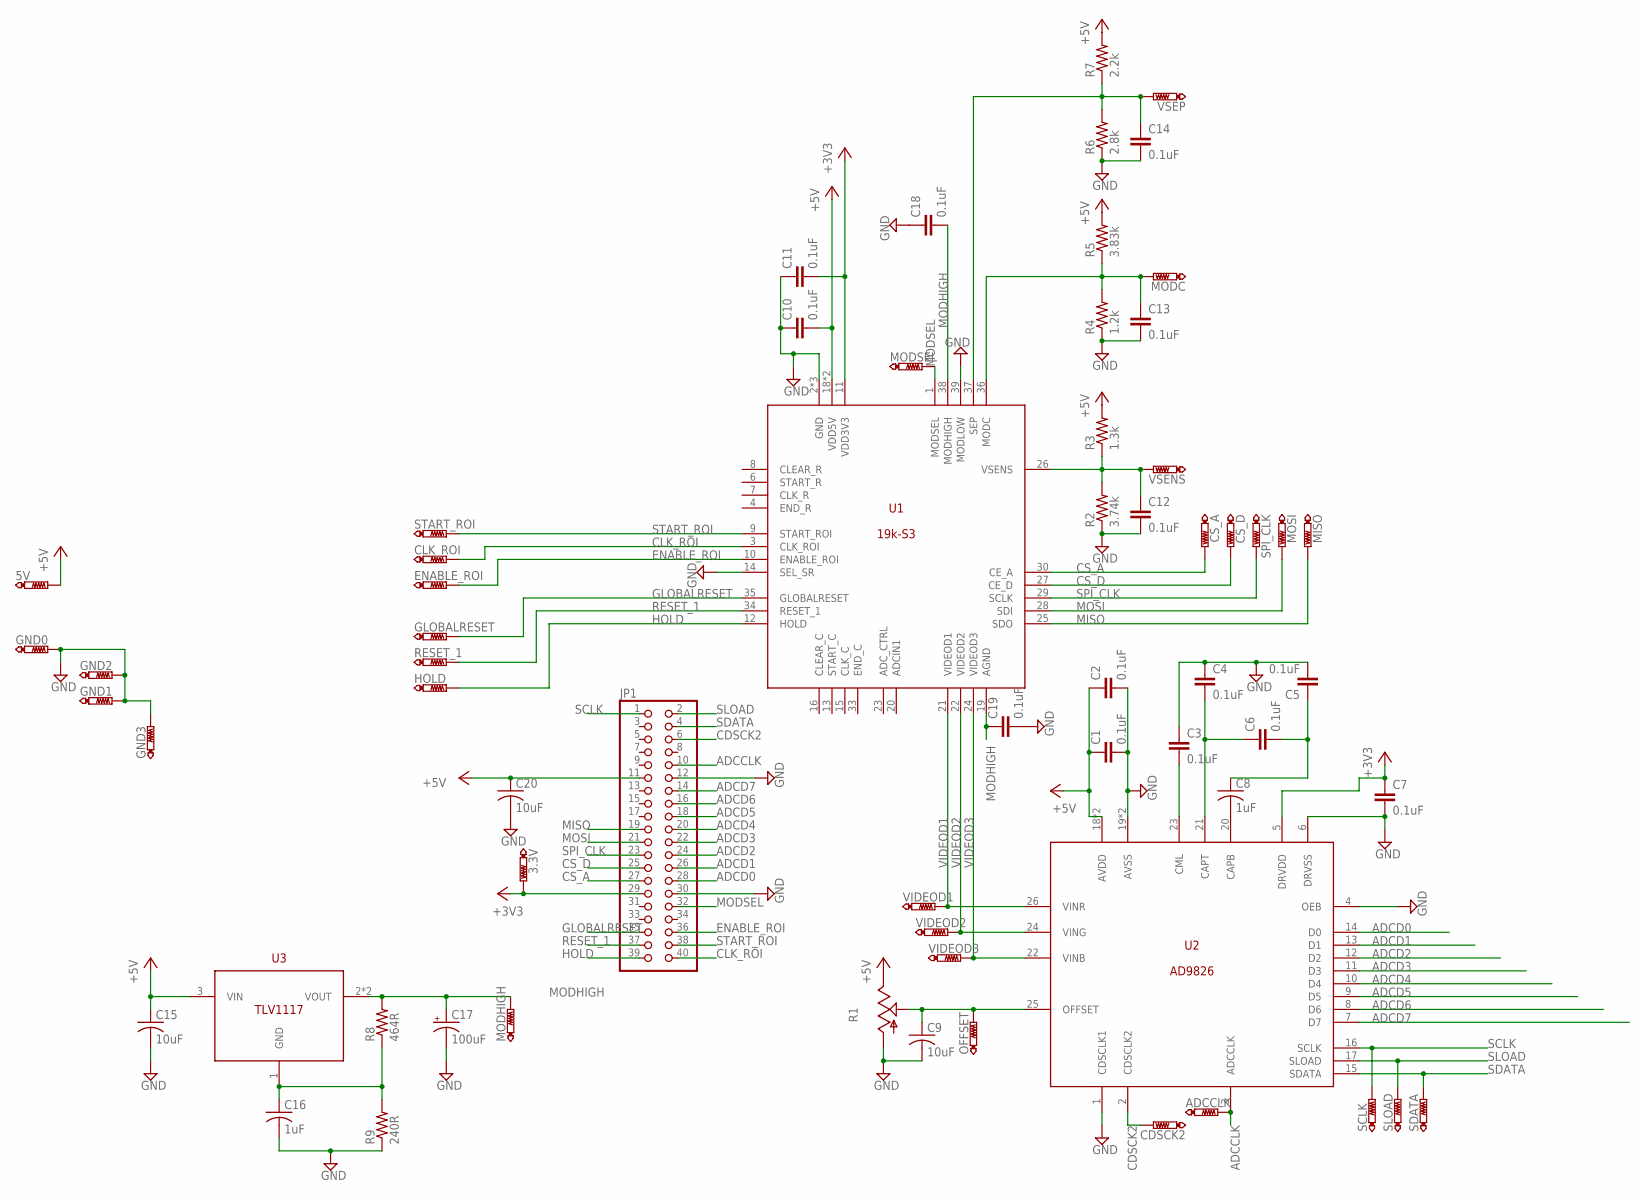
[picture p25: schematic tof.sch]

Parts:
3.3V, 5V: PTR1PAD1-13; P1-13
ADCCLK: PTR1PAD1-13; P1-13
C1, C2, C3, C4, C5, C6, C7, C10, C11, C12, C13, C14, C18, C19: 0.1uF; C0805
C8, C16: 1uF; C0805
C9, C15, C20: 10uF; C0805
C17: 100uF; PANASONIC_F
CDSCK2: PTR1PAD1-13; P1-13
CLK_ROI: PTR1PAD1-13; P1-13
CS_A: PTR1PAD1-13; P1-13
CS_D: PTR1PAD1-13; P1-13
ENABLE_ROI: PTR1PAD1-13; P1-13
GLOBALRESET: PTR1PAD1-13; P1-13
GND0, GND1, GND2, GND3: PTR1PAD1-13; P1-13
HOLD: PTR1PAD1-13; P1-13
JP1: PINHD-2X20; SMD-40
MISO: PTR1PAD1-13; P1-13
MODC: PTR1PAD1-13; P1-13
MODHIGH: PTR1PAD1-13; P1-13
MODSEL: PTR1PAD1-13; P1-13
MOSI: PTR1PAD1-13; P1-13
OFFSET: PTR1PAD1-13; P1-13
R1: TRIM_US-S63P; S63P
R2: 3.74k; R0805
R3: 1.3k; R0805
R4: 1.2k; R0805
R5: 3.83k; R0805
R6: 2.8k; R0805
R7: 2.2k; R0805
R8: 464R; R0805
R9: 240R; R0805
RESET_1: PTR1PAD1-13; P1-13
SCLK: PTR1PAD1-13; P1-13
SDATA: PTR1PAD1-13; P1-13
SLOAD: PTR1PAD1-13; P1-13
SPI_CLK: PTR1PAD1-13; P1-13
START_ROI: PTR1PAD1-13; P1-13
U1: 19K-S3; TLCC40
U2: AD9826; SSOP28
U3: TLV1117; SOT223
VIDEOD1, VIDEOD2, VIDEOD3: PTR1PAD1-13; P1-13
VSENS: PTR1PAD1-13; P1-13
VSEP: PTR1PAD1-13; P1-13

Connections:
+3V3: 3.3V.TP, C7.1, C11.2, JP1.29, U1.11 (VDD3V3), U2.5 (DRVDD)
+5V: 5V.TP, C1.1, C2.1, C10.2, C15.1, C20.1, JP1.11, R1.E, R3.2, R5.2, R7.2, U1.18 (VDD5V), U1.40 (VDD5V), U2.18 (AVDD), U2.28 (AVDD), U3.3 (VIN)
ADCCLK: ADCCLK.TP, JP1.10, U2.3 (ADCCLK)
ADCD0: JP1.28, U2.14 (D0)
ADCD1: JP1.26, U2.13 (D1)
ADCD2: JP1.24, U2.12 (D2)
ADCD3: JP1.22, U2.11 (D3)
ADCD4: JP1.20, U2.10 (D4)
ADCD5: JP1.18, U2.9 (D5)
ADCD6: JP1.16, U2.8 (D6)
ADCD7: JP1.14, U2.7 (D7)
CAPT: C4.2, C6.1, U2.21 (CAPT)
CDSCK2: CDSCK2.TP, JP1.6, U2.2 (CDSCLK2)
CLK_ROI: CLK_ROI.TP, JP1.40, U1.3 (CLK_ROI)
CML: C3.2, U2.23 (CML)
CS_A: CS_A.TP, JP1.27, U1.30 (CE_A)
CS_D: CS_D.TP, JP1.25, U1.27 (CE_D)
ENABLE_ROI: ENABLE_ROI.TP, JP1.36, U1.10 (ENABLE_ROI)
GLOBALRESET: GLOBALRESET.TP, JP1.35, U1.35 (GLOBALRESET)
GND: C1.2, C2.2, C3.1, C4.1, C5.2, C7.2, C9.2, C10.1, C11.1, C12.2, C13.2, C14.2, C15.2, C16.2, C17.-, C18.1, C19.2, C20.2, GND0.TP, GND1.TP, GND2.TP, GND3.TP, JP1.12, JP1.30, R1.A, R2.1, R4.1, R6.1, R9.1, U1.2 (GND), U1.5 (GND), U1.14 (SEL_SR), U1.39 (MODLOW), U1.PAD (GND), U2.1 (CDSCLK1), U2.4 (OEB), U2.6 (DRVSS), U2.19 (AVSS), U2.27 (AVSS)
HOLD: HOLD.TP, JP1.39, U1.12 (HOLD)
MISO: JP1.19, MISO.TP, U1.25 (SDO)
MODHIGH: C17.+, C18.2, C19.1, MODHIGH.TP, R8.2, U1.19 (AGND), U1.38 (MODHIGH), U3.2 (VOUT), U3.4 (VOUT)
MODSEL: JP1.32, MODSEL.TP, U1.1 (MODSEL)
MOSI: JP1.21, MOSI.TP, U1.28 (SDI)
unnamed: C9.1, OFFSET.TP, R1.S, U2.25 (OFFSET)
unnamed: C8.2, U2.20 (CAPB)
unnamed: C5.1, C6.2, C8.1
unnamed: C16.1, R8.1, R9.2, U3.1 (GND)
unnamed: C12.1, R2.2, R3.1, U1.26 (VSENS), VSENS.TP
unnamed: C13.1, MODC.TP, R4.2, R5.1, U1.36 (MODC)
unnamed: C14.1, R6.2, R7.1, U1.37 (SEP), VSEP.TP
RESET_1: JP1.37, RESET_1.TP, U1.34 (RESET_1)
SCLK: JP1.1, SCLK.TP, U2.16 (SCLK)
SDATA: JP1.4, SDATA.TP, U2.15 (SDATA)
SLOAD: JP1.2, SLOAD.TP, U2.17 (SLOAD)
SPI_CLK: JP1.23, SPI_CLK.TP, U1.29 (SCLK)
START_ROI: JP1.38, START_ROI.TP, U1.9 (START_ROI)
VIDEOD1: U1.21 (VIDEOD1), U2.26 (VINR), VIDEOD1.TP
VIDEOD2: U1.22 (VIDEOD2), U2.24 (VING), VIDEOD2.TP
VIDEOD3: U1.24 (VIDEOD3), U2.22 (VINB), VIDEOD3.TP

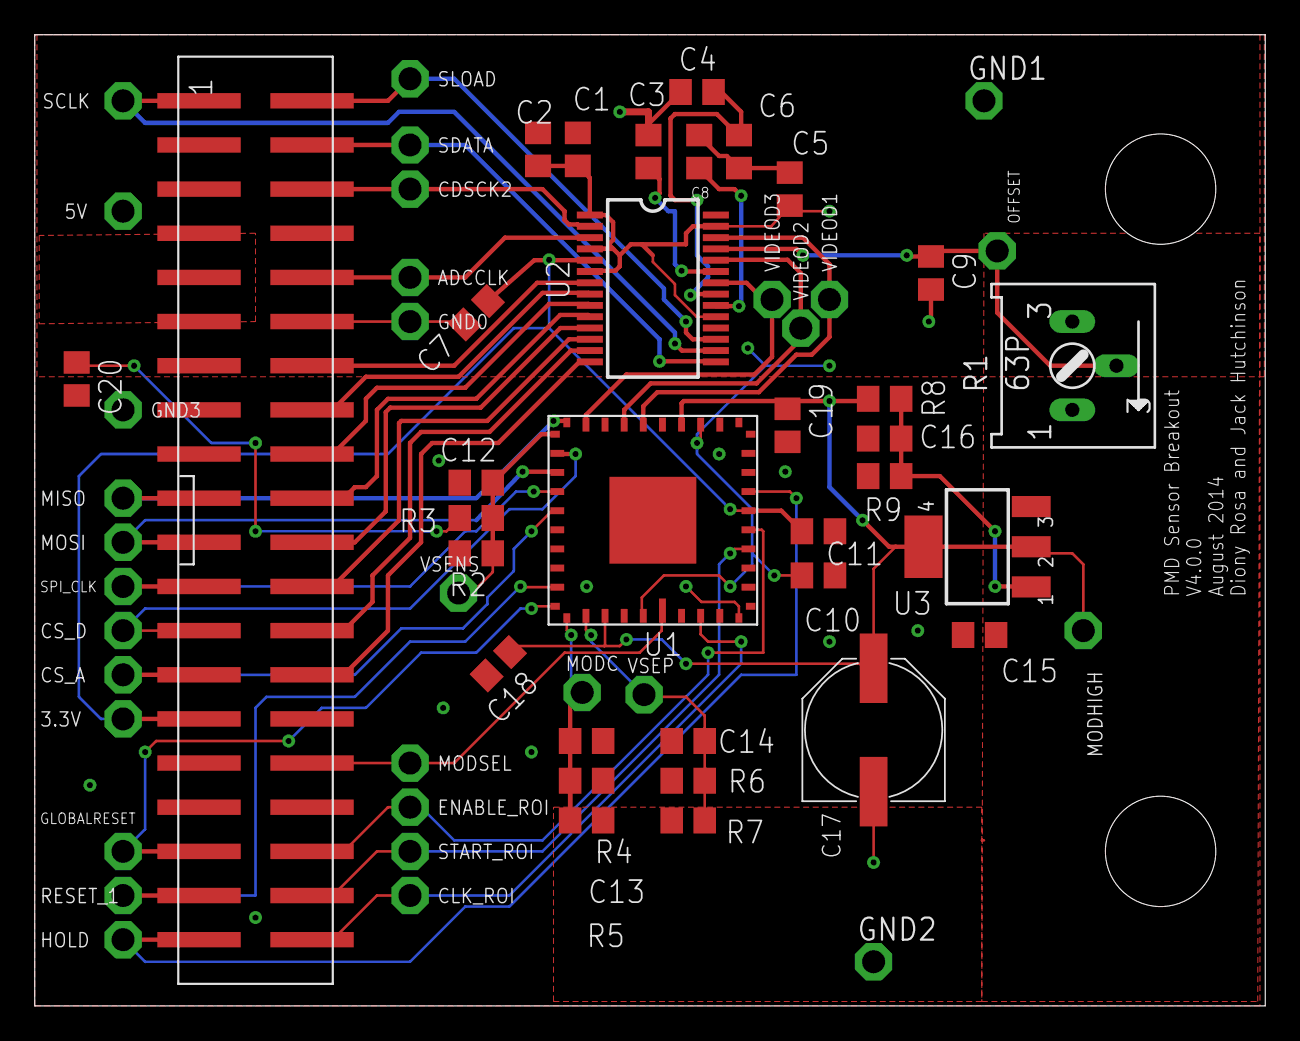
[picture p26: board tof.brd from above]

Board: 2 copper layers, 70.8 x 55.9 mm, 64 parts (0 on the bottom side), 41 nets.

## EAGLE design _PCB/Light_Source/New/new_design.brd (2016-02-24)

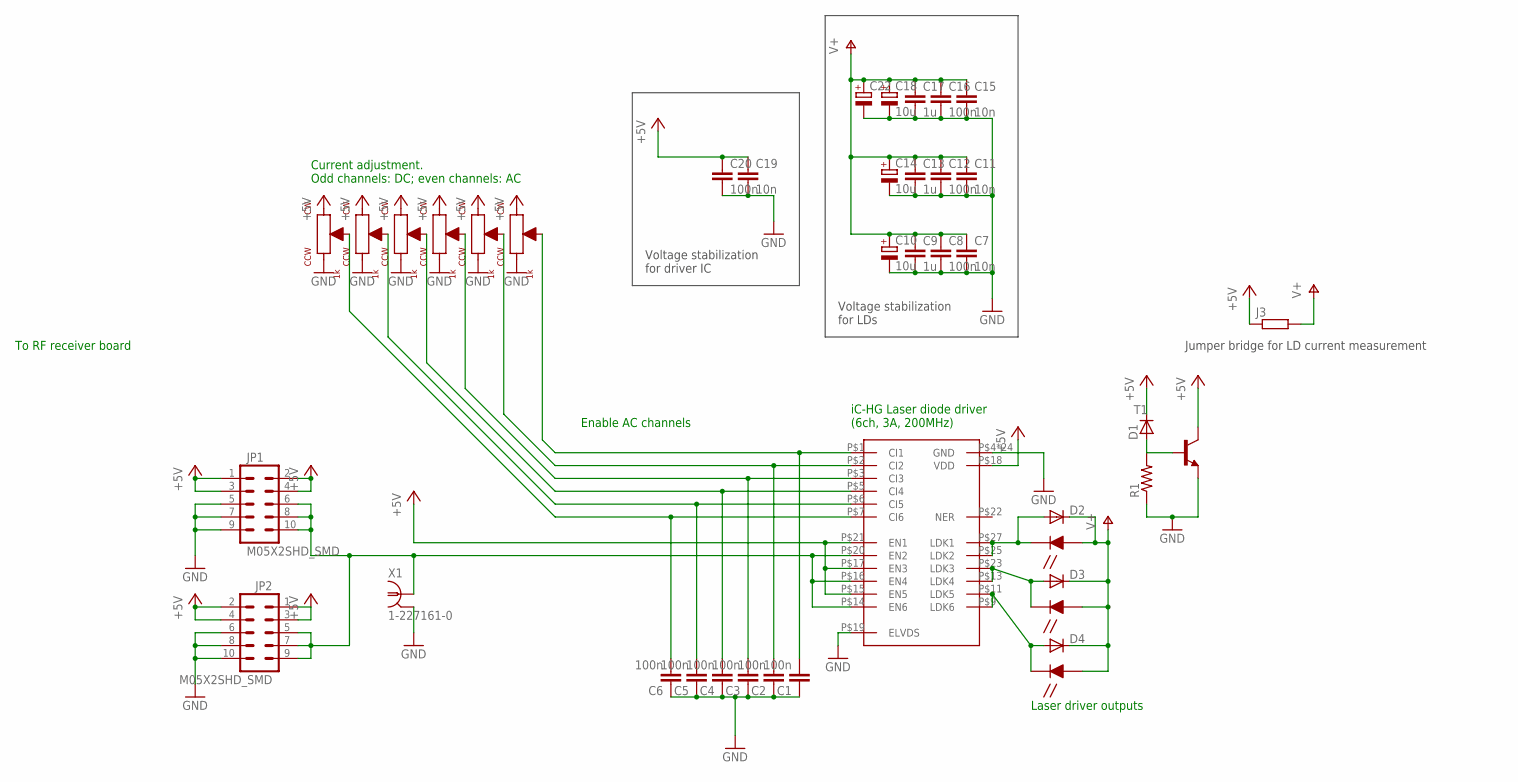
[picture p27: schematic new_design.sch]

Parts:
C1, C2, C3, C4, C5, C6, C8, C12, C16, C20: 100n; C0402K
C7, C11, C15, C19: 10n; C0402K
C9, C13, C17: 1u; C0603
C10, C14, C18: 10u; SMC_B
C22: CPOL-EUCT7343; CT7343
D1: D-SMB; SMB
D2, D3, D4: DIODE-SOD523; SOD523
IC1: IC-HGTHERMAL; QFN28-PAD
J3: R-EU_R1210; R1210
JP1, JP2: M05X2SHD_SMD; 2X5-SHROUDED_SMD
LD1, LD2, LD3: LASER; LD-FLAT
P1, P2, P3, P4, P5, P6: 1k; EVM-1D
R1: RESISTOR0805-RES; 0805
T1: -NPN-SOT223; SOT223
X1: 1-227161-0; AMP_227161

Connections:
+5V: C19.1, C20.1, D1.1 (C), IC1.P$15 (EN5), IC1.P$17 (EN3), IC1.P$18 (VDD), IC1.P$21 (EN1), J3.1, JP1.1, JP1.2, JP1.3, JP1.4, JP2.1, JP2.2, JP2.3, JP2.4, P1.CW, P2.CW, P3.CW, P4.CW, P5.CW, P6.CW, T1.4 (C)
AC_EN: IC1.P$14 (EN6), IC1.P$16 (EN4), IC1.P$20 (EN2), JP1.6, JP1.8, JP1.10, JP2.5, JP2.7, JP2.9, X1.1
GND: C1.1, C2.1, C3.1, C4.1, C5.1, C6.1, C7.2, C8.2, C9.2, C10.-, C11.2, C12.2, C13.2, C14.-, C15.2, C16.2, C17.2, C18.-, C19.2, C20.2, C22.-, IC1.P$4 (GND), IC1.P$8 (GND), IC1.P$10 (GND), IC1.P$12 (GND), IC1.P$19 (ELVDS), IC1.P$24 (GND), IC1.P$26 (GND), IC1.P$28 (GND), IC1.P$29 (GND), IC1.P$30 (GND), IC1.P$31 (GND), IC1.P$32 (GND), IC1.P$33 (GND), IC1.P$34 (GND), IC1.P$35 (GND), IC1.P$36 (GND), IC1.P$37 (GND), IC1.P$38 (GND), IC1.P$39 (GND), IC1.P$40 (GND), IC1.P$41 (GND), IC1.P$42 (GND), IC1.P$43 (GND), IC1.P$44 (GND), IC1.P$45 (GND), JP1.5, JP1.7, JP1.9, JP2.6, JP2.8, JP2.10, P1.CCW, P2.CCW, P3.CCW, P4.CCW, P5.CCW, P6.CCW, R1.1, T1.3 (E), X1.2
unnamed: C2.2, IC1.P$2 (CI2), P2.W
unnamed: C4.2, IC1.P$5 (CI4), P4.W
unnamed: C6.2, IC1.P$7 (CI6), P6.W
unnamed: C1.2, IC1.P$1 (CI1), P1.W
unnamed: C3.2, IC1.P$3 (CI3), P3.W
unnamed: C5.2, IC1.P$6 (CI5), P5.W
unnamed: D4.A, IC1.P$9 (LDK6), IC1.P$11 (LDK5), LD3.C
unnamed: D3.A, IC1.P$13 (LDK4), IC1.P$23 (LDK3), LD2.C
unnamed: D2.A, IC1.P$25 (LDK2), IC1.P$27 (LDK1), LD1.C
unnamed: D1.2 (A), R1.2, T1.1 (B)
V+: C7.1, C8.1, C9.1, C10.+, C11.1, C12.1, C13.1, C14.+, C15.1, C16.1, C17.1, C18.+, C22.+, D2.C, D3.C, D4.C, J3.2, LD1.A, LD2.A, LD3.A

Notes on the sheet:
To RF receiver board
Current adjustment. Odd channels: DC; even channels: AC
Enable AC channels
iC-HG Laser diode driver (6ch, 3A, 200MHz)
Laser driver outputs
Voltage stabilization for LDs
Voltage stabilization for driver IC
Jumper bridge for LD current measurement

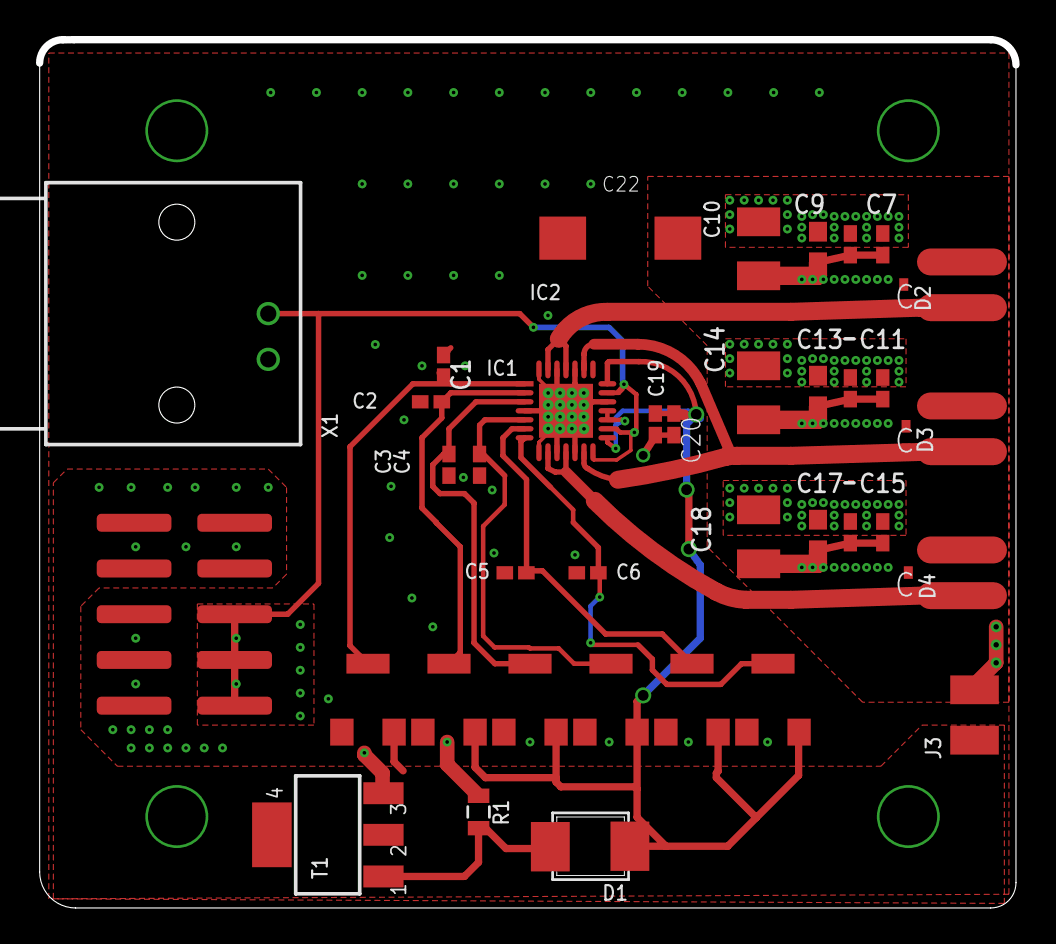
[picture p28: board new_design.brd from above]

Board: 4 copper layers, 54.2 x 48.2 mm, 41 parts (1 on the bottom side), 14 nets.

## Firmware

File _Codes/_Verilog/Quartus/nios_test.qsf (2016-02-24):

# -------------------------------------------------------------------------- #
#
# Copyright (C) 1991-2012 Altera Corporation
# Your use of Altera Corporation's design tools, logic functions 
# and other software and tools, and its AMPP partner logic 
# functions, and any output files from any of the foregoing 
# (including device programming or simulation files), and any 
# associated documentation or information are expressly subject 
# to the terms and conditions of the Altera Program License 
# Subscription Agreement, Altera MegaCore Function License 
# Agreement, or other applicable license agreement, including, 
# without limitation, that your use is for the sole purpose of 
# programming logic devices manufactured by Altera and sold by 
# Altera or its authorized distributors.  Please refer to the 
# applicable agreement for further details.
#
# -------------------------------------------------------------------------- #
#
# Quartus II 32-bit
# Version 12.0 Build 263 08/02/2012 Service Pack 2 SJ Web Edition
# Date created = 20:31:55  June 07, 2014
#
# -------------------------------------------------------------------------- #
#
# Notes:
#
# 1) The default values for assignments are stored in the file:
#		nios_test_assignment_defaults.qdf
#    If this file doesn't exist, see file:
#		assignment_defaults.qdf
#
# 2) Altera recommends that you do not modify this file. This
#    file is updated automatically by the Quartus II software
#    and any changes you make may be lost or overwritten.
#
# -------------------------------------------------------------------------- #


set_global_assignment -name FAMILY "Cyclone IV E"
set_global_assignment -name DEVICE EP4CE115F29C7
set_global_assignment -name TOP_LEVEL_ENTITY top
set_global_assignment -name ORIGINAL_QUARTUS_VERSION "12.0 SP2"
set_global_assignment -name PROJECT_CREATION_TIME_DATE "20:31:55  JUNE 07, 2014"
set_global_assignment -name LAST_QUARTUS_VERSION "12.0 SP2"
set_global_assignment -name MIN_CORE_JUNCTION_TEMP 0
set_global_assignment -name MAX_CORE_JUNCTION_TEMP 85
set_global_assignment -name ERROR_CHECK_FREQUENCY_DIVISOR 1
set_global_assignment -name NOMINAL_CORE_SUPPLY_VOLTAGE 1.2V
set_global_assignment -name POWER_PRESET_COOLING_SOLUTION "23 MM HEAT SINK WITH 200 LFPM AIRFLOW"
set_global_assignment -name POWER_BOARD_THERMAL_MODEL "NONE (CONSERVATIVE)"
set_global_assignment -name PARTITION_NETLIST_TYPE SOURCE -section_id Top
set_global_assignment -name PARTITION_FITTER_PRESERVATION_LEVEL PLACEMENT_AND_ROUTING -section_id Top
set_global_assignment -name PARTITION_COLOR 16764057 -section_id Top
set_global_assignment -name PARTITION_NETLIST_TYPE SOURCE -entity light -section_id Top
set_global_assignment -name PARTITION_FITTER_PRESERVATION_LEVEL PLACEMENT_AND_ROUTING -entity light -section_id Top
set_global_assignment -name PARTITION_COLOR 16764057 -entity light -section_id Top
set_location_assignment PIN_Y2 -to CLOCK_50
set_location_assignment PIN_AG14 -to CLOCK2_50
set_location_assignment PIN_AG15 -to CLOCK3_50
set_location_assignment PIN_AH14 -to SMA_CLKIN
set_location_assignment PIN_AE23 -to SMA_CLKOUT
set_location_assignment PIN_E21 -to LEDG[0]
set_location_assignment PIN_E22 -to LEDG[1]
set_location_assignment PIN_E25 -to LEDG[2]
set_location_assignment PIN_E24 -to LEDG[3]
set_location_assignment PIN_H21 -to LEDG[4]
set_location_assignment PIN_G20 -to LEDG[5]
set_location_assignment PIN_G22 -to LEDG[6]
set_location_assignment PIN_G21 -to LEDG[7]
set_location_assignment PIN_F17 -to LEDG[8]
set_location_assignment PIN_G19 -to LEDR[0]
set_location_assignment PIN_E19 -to LEDR[2]
set_location_assignment PIN_F19 -to LEDR[1]
set_location_assignment PIN_F21 -to LEDR[3]
set_location_assignment PIN_F18 -to LEDR[4]
set_location_assignment PIN_E18 -to LEDR[5]
set_location_assignment PIN_J19 -to LEDR[6]
set_location_assignment PIN_H19 -to LEDR[7]
set_location_assignment PIN_J17 -to LEDR[8]
set_location_assignment PIN_G17 -to LEDR[9]
set_location_assignment PIN_J15 -to LEDR[10]
set_location_assignment PIN_H16 -to LEDR[11]
set_location_assignment PIN_J16 -to LEDR[12]
set_location_assignment PIN_H17 -to LEDR[13]
set_location_assignment PIN_F15 -to LEDR[14]
set_location_assignment PIN_G15 -to LEDR[15]
set_location_assignment PIN_G16 -to LEDR[16]
set_location_assignment PIN_H15 -to LEDR[17]
set_location_assignment PIN_M23 -to KEY[0]
set_location_assignment PIN_M21 -to KEY[1]
set_location_assignment PIN_N21 -to KEY[2]
set_location_assignment PIN_R24 -to KEY[3]
set_location_assignment PIN_AB28 -to SW[0]
set_location_assignment PIN_AC28 -to SW[1]
set_location_assignment PIN_AC27 -to SW[2]
set_location_assignment PIN_AD27 -to SW[3]
set_location_assignment PIN_AB27 -to SW[4]
set_location_assignment PIN_AC26 -to SW[5]
set_location_assignment PIN_AD26 -to SW[6]
set_location_assignment PIN_AB26 -to SW[7]
set_location_assignment PIN_AC25 -to SW[8]
set_location_assignment PIN_AB25 -to SW[9]
set_location_assignment PIN_AC24 -to SW[10]
set_location_assignment PIN_AB24 -to SW[11]
set_location_assignment PIN_AB23 -to SW[12]
set_location_assignment PIN_AA24 -to SW[13]
set_location_assignment PIN_AA23 -to SW[14]
set_location_assignment PIN_AA22 -to SW[15]
set_location_assignment PIN_Y24 -to SW[16]
set_location_assignment PIN_Y23 -to SW[17]
set_location_assignment PIN_G18 -to HEX0[0]
set_location_assignment PIN_F22 -to HEX0[1]
set_location_assignment PIN_E17 -to HEX0[2]
set_location_assignment PIN_L26 -to HEX0[3]
set_location_assignment PIN_L25 -to HEX0[4]
set_location_assignment PIN_J22 -to HEX0[5]
set_location_assignment PIN_H22 -to HEX0[6]
set_location_assignment PIN_M24 -to HEX1[0]
set_location_assignment PIN_Y22 -to HEX1[1]
set_location_assignment PIN_W21 -to HEX1[2]
set_location_assignment PIN_W22 -to HEX1[3]
set_location_assignment PIN_W25 -to HEX1[4]
set_location_assignment PIN_U23 -to HEX1[5]
set_location_assignment PIN_U24 -to HEX1[6]
set_location_assignment PIN_AA25 -to HEX2[0]
set_location_assignment PIN_AA26 -to HEX2[1]
set_location_assignment PIN_Y25 -to HEX2[2]
set_location_assignment PIN_W26 -to HEX2[3]
set_location_assignment PIN_Y26 -to HEX2[4]
set_location_assignment PIN_W27 -to HEX2[5]
set_location_assignment PIN_W28 -to HEX2[6]
set_location_assignment PIN_V21 -to HEX3[0]
set_location_assignment PIN_U21 -to HEX3[1]
set_location_assignment PIN_AB20 -to HEX3[2]
set_location_assignment PIN_AA21 -to HEX3[3]
set_location_assignment PIN_AD24 -to HEX3[4]
set_location_assignment PIN_AF23 -to HEX3[5]
set_location_assignment PIN_Y19 -to HEX3[6]
set_location_assignment PIN_AB19 -to HEX4[0]
set_location_assignment PIN_AA19 -to HEX4[1]
set_location_assignment PIN_AG21 -to HEX4[2]
set_location_assignment PIN_AH21 -to HEX4[3]
set_location_assignment PIN_AE19 -to HEX4[4]
set_location_assignment PIN_AF19 -to HEX4[5]
set_location_assignment PIN_AE18 -to HEX4[6]
set_location_assignment PIN_AD18 -to HEX5[0]
set_location_assignment PIN_AC18 -to HEX5[1]
set_location_assignment PIN_AB18 -to HEX5[2]
set_location_assignment PIN_AH19 -to HEX5[3]
set_location_assignment PIN_AG19 -to HEX5[4]
set_location_assignment PIN_AF18 -to HEX5[5]
set_location_assignment PIN_AH18 -to HEX5[6]
set_location_assignment PIN_AA17 -to HEX6[0]
set_location_assignment PIN_AB16 -to HEX6[1]
set_location_assignment PIN_AA16 -to HEX6[2]
set_location_assignment PIN_AB17 -to HEX6[3]
set_location_assignment PIN_AB15 -to HEX6[4]
set_location_assignment PIN_AA15 -to HEX6[5]
set_location_assignment PIN_AC17 -to HEX6[6]
set_location_assignment PIN_AD17 -to HEX7[0]
set_location_assignment PIN_AE17 -to HEX7[1]
set_location_assignment PIN_AG17 -to HEX7[2]
set_location_assignment PIN_AH17 -to HEX7[3]
set_location_assignment PIN_AF17 -to HEX7[4]
set_location_assignment PIN_AG18 -to HEX7[5]
set_location_assignment PIN_AA14 -to HEX7[6]
set_location_assignment PIN_L6 -to LCD_BLON
set_location_assignment PIN_M5 -to LCD_DATA[7]
set_location_assignment PIN_M3 -to LCD_DATA[6]
set_location_assignment PIN_K2 -to LCD_DATA[5]
set_location_assignment PIN_K1 -to LCD_DATA[4]
set_location_assignment PIN_K7 -to LCD_DATA[3]
set_location_assignment PIN_L2 -to LCD_DATA[2]
set_location_assignment PIN_L1 -to LCD_DATA[1]
set_location_assignment PIN_L3 -to LCD_DATA[0]
set_location_assignment PIN_L4 -to LCD_EN
set_location_assignment PIN_M1 -to LCD_RW
set_location_assignment PIN_M2 -to LCD_RS
set_location_assignment PIN_L5 -to LCD_ON
set_location_assignment PIN_G9 -to UART_TXD
set_location_assignment PIN_G12 -to UART_RXD
set_location_assignment PIN_G14 -to UART_CTS
set_location_assignment PIN_J13 -to UART_RTS
set_location_assignment PIN_G6 -to PS2_KBCLK
set_location_assignment PIN_H5 -to PS2_KBDAT
set_location_assignment PIN_G5 -to PS2_MSCLK
set_location_assignment PIN_F5 -to PS2_MSDAT
set_location_assignment PIN_AE14 -to SD_DAT[0]
set_location_assignment PIN_AF13 -to SD_DAT[1]
set_location_assignment PIN_AB14 -to SD_DAT[2]
set_location_assignment PIN_AC14 -to SD_DAT[3]
set_location_assignment PIN_AE13 -to SD_CLK
set_location_assignment PIN_AD14 -to SD_CMD
set_location_assignment PIN_AF14 -to SD_WP_N
set_location_assignment PIN_D12 -to VGA_B[7]
set_location_assignment PIN_D11 -to VGA_B[6]
set_location_assignment PIN_C12 -to VGA_B[5]
set_location_assignment PIN_A11 -to VGA_B[4]
set_location_assignment PIN_B11 -to VGA_B[3]
set_location_assignment PIN_C11 -to VGA_B[2]
set_location_assignment PIN_A10 -to VGA_B[1]
set_location_assignment PIN_B10 -to VGA_B[0]
set_location_assignment PIN_C9 -to VGA_G[7]
set_location_assignment PIN_F10 -to VGA_G[6]
set_location_assignment PIN_B8 -to VGA_G[5]
set_location_assignment PIN_C8 -to VGA_G[4]
set_location_assignment PIN_H12 -to VGA_G[3]
set_location_assignment PIN_F8 -to VGA_G[2]
set_location_assignment PIN_G11 -to VGA_G[1]
set_location_assignment PIN_G8 -to VGA_G[0]
set_location_assignment PIN_H10 -to VGA_R[7]
set_location_assignment PIN_H8 -to VGA_R[6]
set_location_assignment PIN_J12 -to VGA_R[5]
set_location_assignment PIN_G10 -to VGA_R[4]
set_location_assignment PIN_F12 -to VGA_R[3]
set_location_assignment PIN_D10 -to VGA_R[2]
set_location_assignment PIN_E11 -to VGA_R[1]
set_location_assignment PIN_E12 -to VGA_R[0]
set_location_assignment PIN_A12 -to VGA_CLK
set_location_assignment PIN_F11 -to VGA_BLANK_N
set_location_assignment PIN_C10 -to VGA_SYNC_N
set_location_assignment PIN_G13 -to VGA_HS
set_location_assignment PIN_C13 -to VGA_VS
set_location_assignment PIN_D1 -to AUD_DACDAT
set_location_assignment PIN_E3 -to AUD_DACLRCK
set_location_assignment PIN_D2 -to AUD_ADCDAT
set_location_assignment PIN_C2 -to AUD_ADCLRCK
set_location_assignment PIN_E1 -to AUD_XCK
set_location_assignment PIN_F2 -to AUD_BCLK
set_location_assignment PIN_D14 -to EEP_I2C_SCLK
set_location_assignment PIN_E14 -to EEP_I2C_SDAT
set_location_assignment PIN_B7 -to I2C_SCLK
set_location_assignment PIN_A8 -to I2C_SDAT
set_location_assignment PIN_A17 -to ENET0_GTX_CLK
set_location_assignment PIN_A21 -to ENET0_INT_N
set_location_assignment PIN_C20 -to ENET0_MDC
set_location_assignment PIN_B21 -to ENET0_MDIO
set_location_assignment PIN_C19 -to ENET0_RESET_N
set_location_assignment PIN_A15 -to ENET0_RX_CLK
set_location_assignment PIN_E15 -to ENET0_RX_COL
set_location_assignment PIN_D15 -to ENET0_RX_CRS
set_location_assignment PIN_C16 -to ENET0_RX_DATA[0]
set_location_assignment PIN_D16 -to ENET0_RX_DATA[1]
set_location_assignment PIN_D17 -to ENET0_RX_DATA[2]
set_location_assignment PIN_C15 -to ENET0_RX_DATA[3]
set_location_assignment PIN_C17 -to ENET0_RX_DV
set_location_assignment PIN_D18 -to ENET0_RX_ER
set_location_assignment PIN_B17 -to ENET0_TX_CLK
set_location_assignment PIN_C18 -to ENET0_TX_DATA[0]
set_location_assignment PIN_D19 -to ENET0_TX_DATA[1]
set_location_assignment PIN_A19 -to ENET0_TX_DATA[2]
set_location_assignment PIN_B19 -to ENET0_TX_DATA[3]
set_location_assignment PIN_A18 -to ENET0_TX_EN
set_location_assignment PIN_B18 -to ENET0_TX_ER
set_location_assignment PIN_C23 -to ENET1_GTX_CLK
set_location_assignment PIN_D24 -to ENET1_INT_N
set_location_assignment PIN_D23 -to ENET1_MDC
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

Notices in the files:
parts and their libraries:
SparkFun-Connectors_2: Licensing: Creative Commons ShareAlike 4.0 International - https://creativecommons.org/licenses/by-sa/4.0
